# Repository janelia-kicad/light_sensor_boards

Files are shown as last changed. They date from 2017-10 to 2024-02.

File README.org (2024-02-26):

#+TITLE: light_sensor_boards
#+AUTHOR: Peter Polidoro
#+EMAIL: peter@polidoro.io

* Repository Information
- Name: light_sensor_boards
- Synopsis: Measures fly wingbeats (wing tachometer) using IR light reflected from flapping fly wings.
- URL: https://github.com/janelia-kicad/light_sensor_boards
- Author: Peter Polidoro
- Email:
  - polidorop@janelia.hhmi.org
  - peter@polidoro.io
- License: Janelia Open-Source Hardware
- Version: 2.0
- Release Date: July 2015
- Paper References:
  - Kim, A., Fitzgerald, J. & Maimon, G. Cellular evidence for efference copy in
    Drosophila visuomotor processing. Nat Neurosci 18, 1247–1255 (2015).
    https://doi.org/10.1038/nn.4083
  - David P. Goodman, Abby Eldredge, Catherine R. von Reyn, A novel assay to
    evaluate action selection in escape behavior, Journal of Neuroscience
    Methods, Volume 304, 2018, Pages 154-161, ISSN 0165-0270,
    https://doi.org/10.1016/j.jneumeth.2018.04.019
  - Suver et al., Active antennal movements in Drosophila can tune wind
    encoding, Current Biology (2023), https://doi.org/10.1016/j.cub.2023.01.020

** Description

These light sensor boards, or "wing tachometer”, combine to form a small
electro-optical device that uses reflected infrared light from the fly’s
wingbeats to generate an oscillating voltage signal. The oscillation frequency
of the voltage signal matches, and thus allows one to measure, the tethered
fly's wingbeat frequency.

This device is useful for plate (rather than pin) tethered flight experiments,
because with plate-glued flies, one cannot extract the wingbeat frequency via a
classical wingbeat analyzer. Microphones have also been used for extracting
wingbeat frequency, but they require a quiet room. This wingbeat detector is
immune to audible noise and only requires an infrared light source, often
already present on flight rigs for video recording.

One end of a small diameter light guide is mounted near the fly and aimed at the
wings. The other end of the light guide is in a small enclosure containing an
optical filter and printed circuit board and can be mounted off to the side of
the rig wherever there is room.

The light guide brings light reflected off of the wings down to a photodiode on
a circuit board, after passing through an optical filter to remove the unwanted
wavelengths of light. Amplifiers and filters on the circuit board convert the
tiny amounts of current from the photodiode into an oscillating voltage signal,
with a frequency range of several hundred Hertz and a magnitude range of several
Volts.

The oscillating voltage signal can be fed into a data acquisition card,
oscilloscope, and/or a speaker for recording and instant feedback on fly
wingbeat frequency. Using a threshold, the signal can be used as a simple
boolean that indicates whether the tethered animal is flying or not for
triggering experiments or synchronizing the data collection.

This device was first created at Caltech in the Dickinson lab in collaboration
with Gaby Maimon around 2010. It has transformed over several generations,
getting smaller and more robust each iteration. It has been used on rigs in
multiple universities and research institutes and has been referenced in several
papers. Version 2 was designed in collaboration with Sung Soo Kim and the Card
lab at Janelia Research Campus.

These boards have been deprecated and some parts are now difficult to purchase
or are obsolete.

The files in this repository are archived for reference.

* opt101 + power_signal

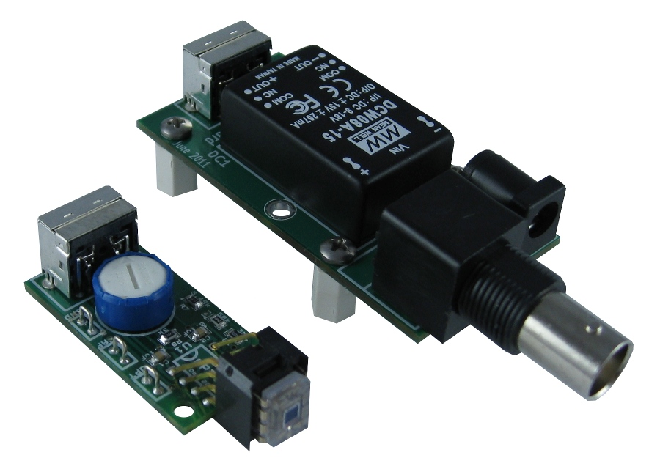
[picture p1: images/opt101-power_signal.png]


* opt101 + power_signal_compare

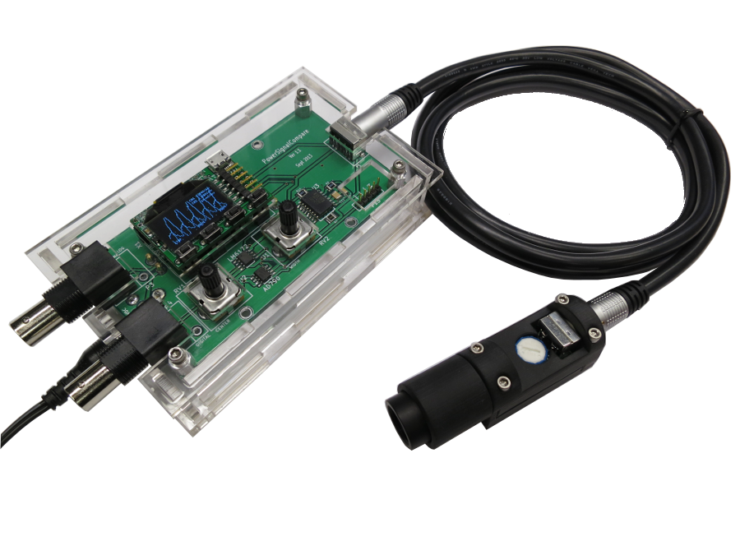
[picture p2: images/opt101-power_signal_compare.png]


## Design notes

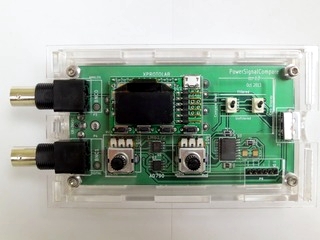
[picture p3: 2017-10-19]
light_sensor_boards/images/light_sensor_boards_19_s.jpg

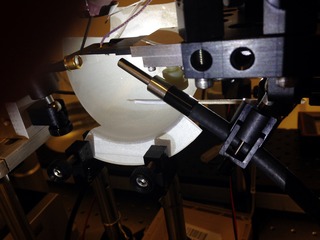
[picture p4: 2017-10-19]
light_sensor_boards/images/light_sensor_boards_24_s.jpg

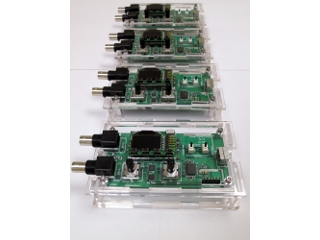
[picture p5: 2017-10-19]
light_sensor_boards/images/light_sensor_boards_20_s.jpg

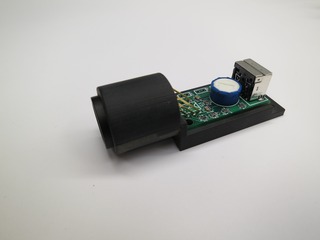
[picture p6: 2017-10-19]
light_sensor_boards/images/light_sensor_boards_06_s.jpg

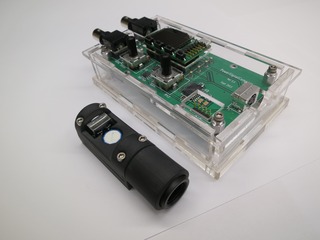
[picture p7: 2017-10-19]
light_sensor_boards/images/light_sensor_boards_02_s.jpg

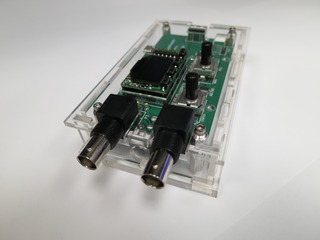
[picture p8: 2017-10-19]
light_sensor_boards/images/light_sensor_boards_12_s.jpg

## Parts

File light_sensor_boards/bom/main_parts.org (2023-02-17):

| Descripition                                                | Digi-Key Part Number |
|-------------------------------------------------------------+----------------------|
| CONN RCPT FMALE MINI DIN 4P SLDR                            | CP-2245-ND           |
| CBL 4POS MALE TO MALE 4.92'                                 | AE10074-ND           |
| CONN PWR JACK 2X5.5MM SOLDER                                | CP-063AH-ND          |
| DC DC CONVERTER 5V +/-15V 11W                               | 811-1827-5-ND        |
| IC FILTER 100KHZ UNIV 16SOIC                                | UAF42AU-ND           |
| TRIMMER 10K OHM 1W PC PIN TOP                               | 3345P-103-ND         |
| Optical Sensor Ambient 650nm Voltage 8-DIP (0.300", 7.62mm) | 296-23090-5-ND       |
| CONN IC DIP SOCKET 8POS GOLD                                | A117-ND              |

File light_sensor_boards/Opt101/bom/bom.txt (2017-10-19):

-*- mode:org -*-

# Opt101.lst
| ref | value  |
|-----+--------|
| C1  | 0.1uF  |
| C2  | 0.1uF  |
| C3  | 0.1uF  |
| C4  | 0.1uF  |
| J1  | DIN_4  |
| PP1 | OPT    |
| PP2 | UAF    |
| PP3 | GND    |
| R1  | 3M     |
| R2  | 42.2k  |
| R3  | 2.55M  |
| R4  | 2.55M  |
| R5  | 10     |
| R6  | 50k    |
| R7  | 5.49k  |
| R8  | 5k     |
| RV1 | 10k    |
| U1  | OPT101 |
| U3  | UAF42  |

# Bill of Materials
| ! | part  | description                     | vendor       | part number      | quantity |  cost |
|---+-------+---------------------------------+--------------+------------------+----------+-------|
|   | PCB   | OPT101 2.0                      | protoexpress | afv1-32881       |        1 | 35.00 |
|   | C1-4  | CAP CERM .1UF 10% 50V X7R 0805  | digikey      | 478-1395-1-ND    |        4 |  0.05 |
|   | J1    | CONN MINI-DIN 4PIN R/A SLIM PCB | digikey      | CP-2245-ND       |        1 |  1.82 |
|   | PP1-3 | JUMPER WIRE 0.1" LONG           | digikey      | 923345-01-ND     |        3 |  0.07 |
|   | R1    | RES 3.00M OHM 1/8W 1% 0805 SMD  | digikey      | 541-3.00MCCT-ND  |        1 |  0.09 |
|   | R2    | RES 42.2K OHM 1/8W 1% 0805 SMD  | digikey      | P42.2KCCT-ND     |        1 |  0.07 |
|   | R3,4  | RES 2.55M OHM 1/8W 1% 0805 SMD  | digikey      | 311-2.55MCRCT-ND |        2 |  0.03 |
|   | R5    | RES 10.0 OHM 1/8W 1% 0805 SMD   | digikey      | P10.0CCT-ND      |        1 |  0.07 |
|   | R6    | RES 49.9K OHM 1/8W 1% 0805 SMD  | digikey      | P49.9KCCT-ND     |        1 |  0.07 |
|   | R7    | RES 5.49K OHM 1/8W 1% 0805 SMD  | digikey      | P5.49KCCT-ND     |        1 |  0.07 |
|   | R8    | RES 4.99K OHM 1/8W 1% 0805 SMD  | digikey      | P4.99KCCT-ND     |        1 |  0.07 |
|   | RV1   | TRIMMER 10K OHM 1W TH           | digikey      | 3345P-103-ND     |        1 | 13.02 |
|   | U1    | IC PHOTODIODE/AMPLIFIER 8 DIP   | digikey      | 296-23090-5-ND   |        1 |  6.88 |
|   | U1    | IC SOCK 8 PIN VERT GOLD .300    | digikey      | A117-ND          |        1 |  6.29 |
|   | U3    | IC UNIV ACTIVE FILTER 16-SOIC   | digikey      | UAF42AU-ND       |        1 | 16.61 |
|---+-------+---------------------------------+--------------+------------------+----------+-------|
| # | total |                                 |              |                  |          | 80.53 |
#+TBLFM: @17$7=(@I$quantity..@II$quantity)*(@I$cost..@II$cost);%.2f;N

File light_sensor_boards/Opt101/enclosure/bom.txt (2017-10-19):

-*- mode:org -*-

# Bill of Materials
| ! | description                                                                            | vendor       | part number | quantity |   cost |
|---+----------------------------------------------------------------------------------------+--------------+-------------+----------+--------|
|   | SM05 Lens Tube, 0.5" Thread Depth                                                      | thorlabs     | SM05L05     |        1 |  13.75 |
|   | Liquid Light Guide Ø3 mm Core, 4' (1.2 m) Length                                       | thorlabs     | LLG0338-4   |        1 | 345.00 |
|   | Ø3 mm LLG to SM1 Adapter                                                               | thorlabs     | AD3LLG      |        1 |  30.00 |
|   | Adapter with External SM05 Threads and Internal SM1 Threads                            | thorlabs     | SM1A1       |        1 |  19.75 |
|   | Universal probe holder                                                                 | siskiyou     | MXB         |        1 | 200.00 |
|   | 850nm High Performance Longpass Filter 12.5mm Dia                                      | edmundoptics | 66-228      |        1 | 150.00 |
|   | 18-8 Stainless Steel Socket Head Cap Screw, 4-40 Thread, 3/4" Length                   | mcmaster     | 92196A113   |        4 |   0.06 |
|   | 18-8 Stainless Steel Machine Screw Hex Nut, 4-40 Thread Size, 1/4" Width, 3/32" Height | mcmaster     | 91841A005   |        4 |   0.03 |
|---+----------------------------------------------------------------------------------------+--------------+-------------+----------+--------|
| # | total                                                                                  |              |             |          | 758.86 |
#+TBLFM: @10$6=(@I$quantity..@II$quantity)*(@I$cost..@II$cost);%.2f;N

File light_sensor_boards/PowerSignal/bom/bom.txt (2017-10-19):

-*- mode:org -*-

# PowerSignal.lst
| ref | value        |
|-----+--------------|
| C1  | 10uF         |
| C2  | 1uF          |
| C3  | 10uF         |
| C4  | 1uF          |
| C5  | 0.1uF        |
| C6  | 0.1uF        |
| C7  | 0.1uF        |
| DC1 | DCW08        |
| P1  | DIN_4_SHIELD |
| P2  | BNC          |
| P3  | 9-18VDC      |
| P4  | CONN_1       |
| P5  | CONN_1       |
| P6  | CONN_1       |
| P7  | CONN_1       |
| P8  | CONN_1       |
| P9  | CONN_1       |
| P10 | CONN_1       |
| R1  | 634          |
| U1  | BUF634       |

# Bill of Materials
| ! | part  | description                      | vendor       | part number    | quantity |  cost |
|---+-------+----------------------------------+--------------+----------------+----------+-------|
|   | PCB   | PowerSignal 2.1                  | protoexpress | afv1-60094     |        1 | 34.50 |
|   | C1,3  | CAP CER 10UF 50V X7S 1210        | digikey      | 445-4536-1-ND  |        2 |  1.24 |
|   | C2,4  | CAP CER 1.0UF 50V 10% X7R 1210   | digikey      | 490-1863-1-ND  |        2 |  0.48 |
|   | C5-7  | CAP CERM .10UF 10% 50V X7R 1210  | digikey      | 478-3586-1-ND  |        3 |  0.73 |
|   | DC1   | DC-DC 2 Output 15 Volt-15 Volt   | jameco       | 1953364        |        1 | 19.95 |
|   | P1    | CONN MINI-DIN 4PIN R/A SLIM PCB  | digikey      | CP-2245-ND     |        1 |  1.82 |
|   | P1    | S-VIDEO 6'CABLE,2X MALE PLUGS    | jameco       | 228591         |        1 |  2.15 |
|   | P2    | CONN SOCKET BNC R/A 50 OHM PCB   | digikey      | A97555-ND      |        1 |  2.30 |
|   | P3    | Male 2 Position 6mm 2 Terminal   | jameco       | 137673         |        1 |  0.45 |
|   | P3    | AC/DC Power Supply 12V 1A 12W    | jameco       | 252824         |        1 | 12.95 |
|   | P4-10 | STDOFF HEX FLA-RET 4-40 .375"L   | digikey      | 8440BK-ND      |        5 |  0.84 |
|   | P4-10 | SCREW MACHINE PHIL 4-40X1/4 SS   | digikey      | H703-ND        |        5 |  0.05 |
|   | R1    | RES 634 OHM 1/4W 1% 1210 SMD     | digikey      | RHM634BDCT-ND  |        1 |  0.36 |
|   | U1    | IC OPAMP BUFFER 180MHZ SGL 8SOIC | digikey      | 296-24142-1-ND |        1 |  9.28 |
|---+-------+----------------------------------+--------------+----------------+----------+-------|
| # | total |                                  |              |                |          | 93.84 |
#+TBLFM: @16$7=(@I$quantity..@II$quantity)*(@I$cost..@II$cost);%.2f;N

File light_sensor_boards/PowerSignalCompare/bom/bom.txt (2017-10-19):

-*- mode:org -*-

# PowerSignalCompare.lst
| ref | value             |
|-----+-------------------|
| C1  | 22uF              |
| C2  | 22uF              |
| C3  | 22uF              |
| C4  | 47uF              |
| C5  | 0.1uF             |
| C6  | 0.1uF             |
| C7  | 0.1uF             |
| C8  | 0.1uF             |
| C9  | 0.1uF             |
| C10 | 0.1uF             |
| C11 | 0.1uF             |
| C12 | 0.1uF             |
| C13 | 0.1uF             |
| C14 | 0.1uF             |
| D1  | 9.1V_ZENER        |
| D2  | 9.1V_ZENER        |
| P1  | DIN_4_SHIELD      |
| P2  | 18-36VDC          |
| P3  | BNC0              |
| P4  | BNC1              |
| P5  | CONN_1            |
| P6  | CONN_1            |
| P7  | CONN_1            |
| P8  | CONN_1            |
| P9  | CONN_6            |
| R1  | 1k                |
| R2  | 1k                |
| R3  | 220               |
| R4  | 220               |
| R5  | 634               |
| R6  | 510               |
| R7  | 50k               |
| R8  | 44.2k             |
| R9  | 402k              |
| R10 | 402k              |
| RV1 | 10k               |
| RV2 | 10k               |
| S1  | TWR_TRIPLE_SUPPLY |
| SW1 | DISPLAY           |
| SW2 | COMPARE_INPUT     |
| U1  | LM6172            |
| U2  | AD790             |
| U3  | UAF42             |
| U4  | ISL55004          |
| X1  | XPROTOLAB         |

# Bill of Materials
| ! | part  | description                      | vendor      | part number         | quantity |   cost |
|---+-------+----------------------------------+-------------+---------------------+----------+--------|
|   | PCB   | PowerSignalCompare_v1.3          | pcbuniverse |                     |        1 |      0 |
|   | C1    | CAP TANT 22UF 50V 20% 2917       | digikey     | 399-9752-1-ND       |        1 |   5.45 |
|   | C2-3  | CAP TANT 22UF 20V 10% 1210       | digikey     | 478-3095-1-ND       |        2 |   1.27 |
|   | C4    | CAP TANT 47UF 10V 20% 1210       | digikey     | 478-3132-1-ND       |        1 |   1.24 |
|   | C5-14 | CAP CERM .10UF 10% 50V X7R 1210  | digikey     | 478-3586-1-ND       |       10 |   0.34 |
|   | D1-2  | DIODE ZENER 9.1V 250MW TO236AB   | digikey     | 568-7102-1-ND       |        2 |   0.49 |
|   | P1    | CONN MINI-DIN 4PIN R/A SLIM PCB  | digikey     | CP-2245-ND          |        1 |   1.79 |
|   | P1    | CABLE VIDEO S-VHS HI QUAL 1.5M   | digikey     | AE10074-ND          |        1 |   8.34 |
|   | P2    | CONN PWR JACK DC 2.1X5.5 8A T/H  | digikey     | CP-063AH-ND         |        1 |   1.78 |
|   | P2    | TRANSFORMER DESK TOP 24V 40W     | digikey     | T1206-P5P-ND        |        1 |  21.76 |
|   | P3-4  | CONN SOCKET BNC R/A 50 OHM PCB   | digikey     | A97555-ND           |        2 |   2.62 |
|   | P9    | CONN HEADER 6POS .100" SGL GOLD  | digikey     | SAM1031-06-ND       |        1 |   0.95 |
|   | R1-2  | RES 1K OHM 1/4W 1% 1210 SMD      | digikey     | RHM1.00KBDCT-ND     |        2 |   0.23 |
|   | R3-4  | RES 220 OHM 1/4W .1% 1210 SMD    | digikey     | P220QCT-ND          |        2 |   1.10 |
|   | R5    | RES 634 OHM 1/4W 1% 1210 SMD     | digikey     | RHM634BDCT-ND       |        1 |   0.23 |
|   | R6    | RES 510 OHM 1/4W .1% 1210 SMD    | digikey     | P510QCT-ND          |        1 |   1.10 |
|   | R7    | RES 49.9K OHM 1/4W 1% 1210 SMD   | digikey     | RHM49.9KBDCT-ND     |        1 |   0.23 |
|   | R8    | RES 44.2K OHM 1/2W 1% 1210 SMD   | digikey     | P44.2KAACT-ND       |        1 |   0.51 |
|   | R9-10 | RES 402K OHM 1/2W 1% 1210 SMD    | digikey     | P402KAACT-ND        |        2 |   0.51 |
|   | RV1-2 | POT 10K OHM 1/8W CARB VERTICAL   | digikey     | CT2265-ND           |        2 |   1.55 |
|   | S1    | CONV DC/DC TRI OUT 5,15,-15V     | digikey     | 811-1827-5-ND       |        1 |  75.60 |
|   | S1    | CONN RECEPT PIN .032-.046" .296" | digikey     | ED90531-ND          |        5 |   1.04 |
|   | SW1-2 | SWITCH TOGGLE SPDT 0.4VA 20V     | digikey     | CKN1784CT-ND        |        2 |   5.63 |
|   | U1    | IC AMP DUAL HI SPD LP V FB 8SOIC | digikey     | LM6172IMX/NOPBCT-ND |        1 |   3.94 |
|   | U2    | IC COMPARATOR PREC W/LATCH 8SOIC | digikey     | AD790JRZ-REEL7CT-ND |        1 |   8.61 |
|   | U3    | IC UNIV ACTIVE FILTER 16-SOIC    | digikey     | UAF42AU-ND          |        1 |  14.95 |
|   | U4    | IC OPAMP QUAD 200MHZ 14-SOIC     | digikey     | ISL55004IBZ-ND      |        1 |   9.45 |
|   | X1    | CONN HEADER FMALE 12POS .1" GOLD | digikey     | S7045-ND            |        1 |   0.99 |
|   | X1    | CONN HEADER FEMALE 2POS .1" GOLD | digikey     | S7035-ND            |        4 |   0.49 |
|   | X1    | XMEGA Xprotolab                  | gabotronics | XMEGA Xprotolab     |        1 |  49.00 |
|---+-------+----------------------------------+-------------+---------------------+----------+--------|
| # | total |                                  |             |                     |          | 243.28 |
#+TBLFM: @32$7=(@I$quantity..@II$quantity)*(@I$cost..@II$cost);%.2f;N

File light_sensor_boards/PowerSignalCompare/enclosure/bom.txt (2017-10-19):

-*- mode:org -*-
# Bill of Materials
| ! | description                                                                                                  | vendor   | part number | quantity |  cost |
|---+--------------------------------------------------------------------------------------------------------------+----------+-------------+----------+-------|
|   | Optically Clear Cast Acrylic Sheet, 1/8" Thick, 12" x 12"                                                    | mcmaster | 8560K239    |        1 |  8.63 |
|   | Optically Clear Cast Acrylic Sheet, 1/4" Thick, 12" x 12"                                                    | mcmaster | 8560K354    |        1 | 16.36 |
|   | 18-8 Stainless Steel Socket Head Cap Screw, 4-40 Thread, 5/16" Length                                        | mcmaster | 92196A107   |        4 |  0.04 |
|   | 300 Series Stainless Steel NAS 620 Flat Washer, Number 4 Size, .21" OD, .01"-.02" Thickness, Dash Number C4L | mcmaster | 90945A710   |        4 |  0.01 |
|   | 18-8 Stainless Steel Male-Female Threaded Hex Standoff, 3/16" Hex, 1/2" Length, 4-40 Screw Size              | mcmaster | 91075A665   |        4 |  2.20 |
|   | 18-8 Stainless Steel Male-Female Threaded Hex Standoff, 3/16" Hex, 1/4" Length, 4-40 Screw Size              | mcmaster | 91075A655   |        4 |  2.15 |
|---+--------------------------------------------------------------------------------------------------------------+----------+-------------+----------+-------|
| # |                                                                                                              |          |             |          | 42.59 |
#+TBLFM: @8$6=(@I$quantity..@II$quantity)*(@I$cost..@II$cost);%.2f;N

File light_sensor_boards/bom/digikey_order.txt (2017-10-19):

12, 399-9752-1-ND
25, 478-3095-1-ND
12, 478-3132-1-ND
120, 478-3586-1-ND
25, CP-2245-ND
12, AE10074-ND
12, CP-063AH-ND
12, T1073-P5P-ND
25, A97555-ND
12, SAM1031-05-ND
25, RHM1.00KBDCT-ND
25, P220QCT-ND
25, RHM634BDCT-ND
25, P510QCT-ND
25, RHM49.9KBDCT-ND
25, P44.2KAACT-ND
25, P402KAACT-ND
25, CT2265-ND
12, 811-1827-5-ND
12, LM6172IMX/NOPBCT-ND
12, AD790JRZ-REEL7CT-ND
25, UAF42AU-ND
12, ISL55004IBZ-ND
20, S7045-ND
50, S7035-ND
100, 478-1395-1-ND
100, 541-3.00MCCT-ND  
100, P42.2KCCT-ND     
100, 311-2.55MCRCT-ND 
100, P10.0CCT-ND      
100, P49.9KCCT-ND     
100, P5.49KCCT-ND     
100, P4.99KCCT-ND     
20, 3345P-103-ND     
20, 296-23090-5-ND   
20, A117-ND

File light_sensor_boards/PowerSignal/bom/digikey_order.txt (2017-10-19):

20, 445-4536-1-ND
20, 490-1863-1-ND
20, 478-3586-1-ND
20, CP-2245-ND
20, A97555-ND
100, 8440BK-ND
100, H703-ND
20, RHM634BDCT-ND
20, 296-24142-1-ND

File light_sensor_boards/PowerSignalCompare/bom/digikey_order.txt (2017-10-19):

12, 399-9752-1-ND
25, 478-3095-1-ND
12, 478-3132-1-ND
200, 478-3586-1-ND
25, 568-7102-1-ND
12, CP-2245-ND
4, AE10074-ND
12, CP-063AH-ND
2, T1206-P5P-ND
25, A97555-ND
12, SAM1031-06-ND
25, RHM1.00KBDCT-ND
25, P220QCT-ND
25, RHM634BDCT-ND
25, P510QCT-ND
25, RHM49.9KBDCT-ND
25, P44.2KAACT-ND
25, P402KAACT-ND
30, CT2265-ND
10, 811-1827-5-ND
75, ED90531-ND
25, CKN1784CT-ND
15, LM6172IMX/NOPBCT-ND
15, AD790JRZ-REEL7CT-ND
12, UAF42AU-ND
12, ISL55004IBZ-ND
20, S7045-ND
75, S7035-ND

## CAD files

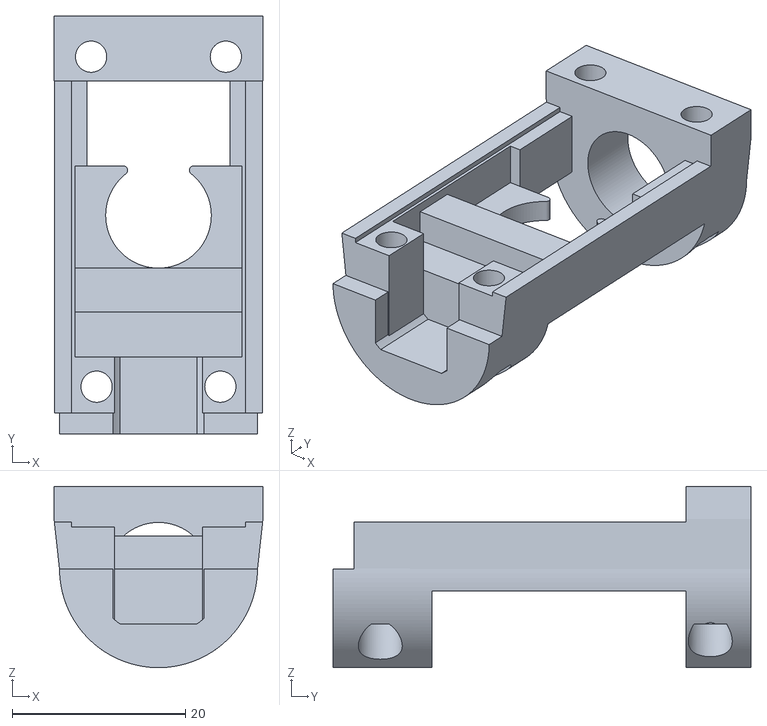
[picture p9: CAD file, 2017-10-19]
light_sensor_boards/Opt101/enclosure/Opt101EnclosureFront.stl
24.1 x 48.3 x 20.9

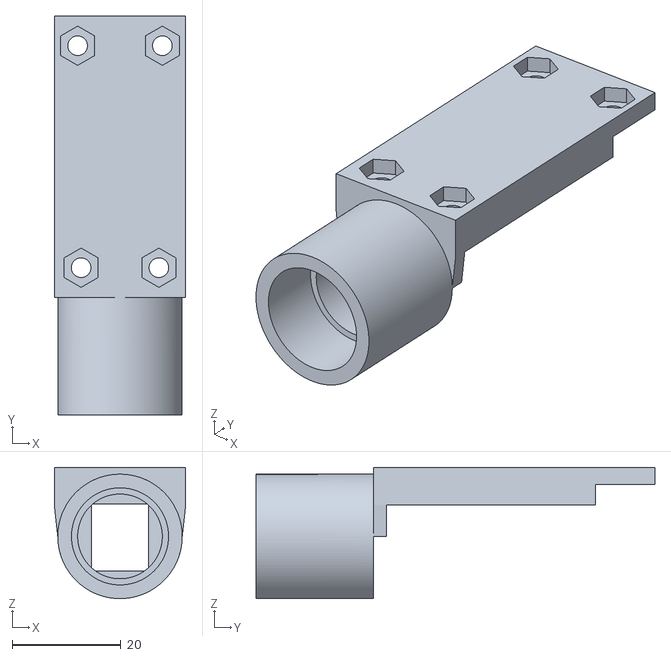
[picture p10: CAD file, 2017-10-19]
light_sensor_boards/Opt101/stl/Opt101EnclosureBack.stl
24.1 x 73.3 x 24.1

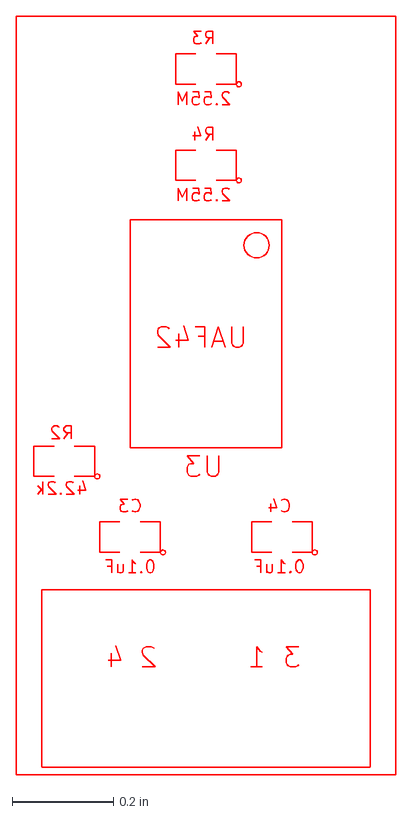
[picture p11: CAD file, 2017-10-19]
light_sensor_boards/Opt101/v2.0/dxf/Opt101-SilkS_Back.dxf
0.75 x 1.50 in

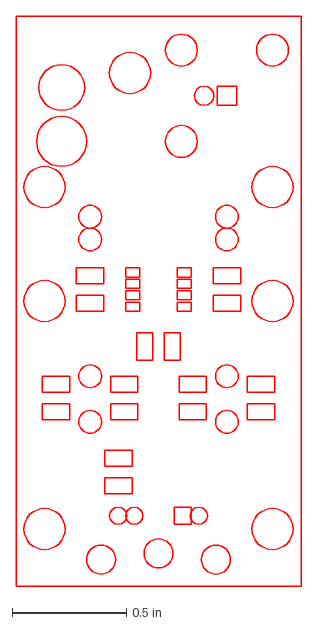
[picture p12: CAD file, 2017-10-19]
light_sensor_boards/PowerSignal/v2.1/dxf/PowerSignal-Mask_Back.dxf
1.25 x 2.50 in

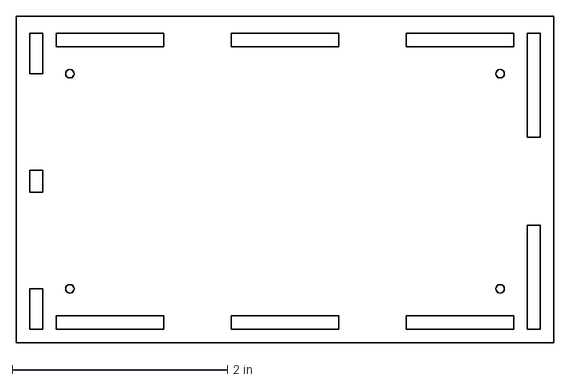
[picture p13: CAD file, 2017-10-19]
light_sensor_boards/PowerSignalCompare/enclosure/PowerSignalCompareEnclosure.25in.dxf
5.00 x 3.03 in

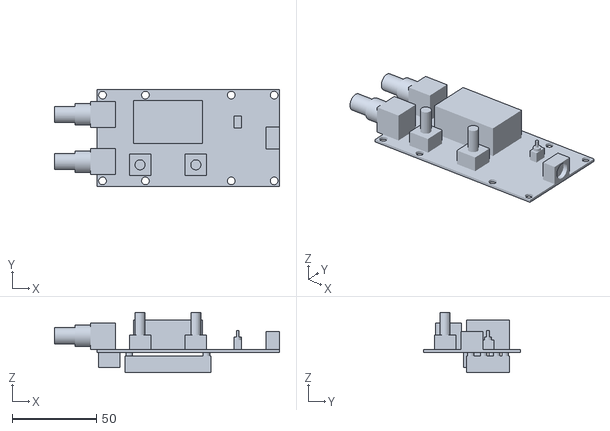
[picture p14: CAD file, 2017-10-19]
light_sensor_boards/PowerSignalCompare/stl/PowerSignalCompare.stl
133.2 x 57.1 x 35.8

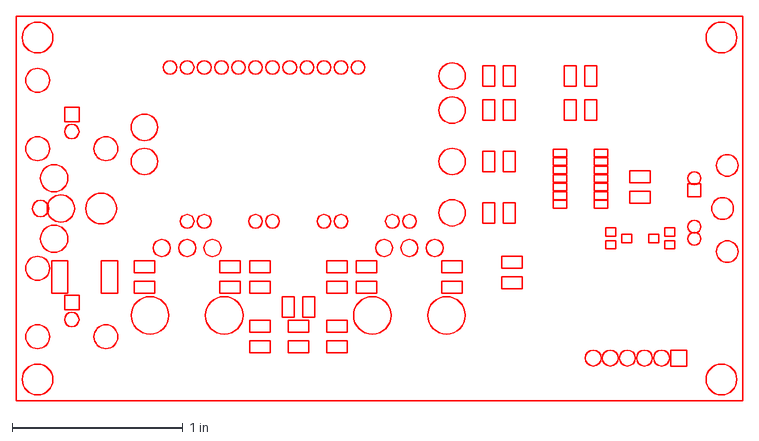
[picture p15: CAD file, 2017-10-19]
light_sensor_boards/PowerSignalCompare/v1.3/dxf/PowerSignalCompare-Mask_Back.dxf
4.25 x 2.25 in

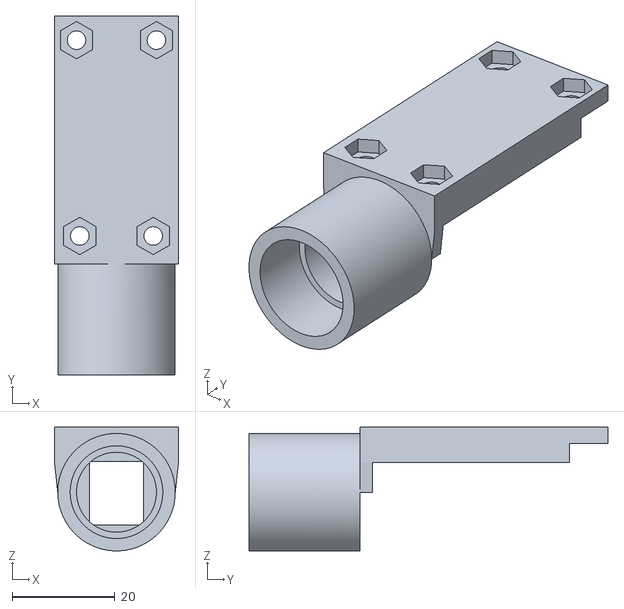
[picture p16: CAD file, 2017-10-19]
light_sensor_boards/Opt101/enclosure/Opt101EnclosureBack.stl
24.1 x 69.8 x 24.1

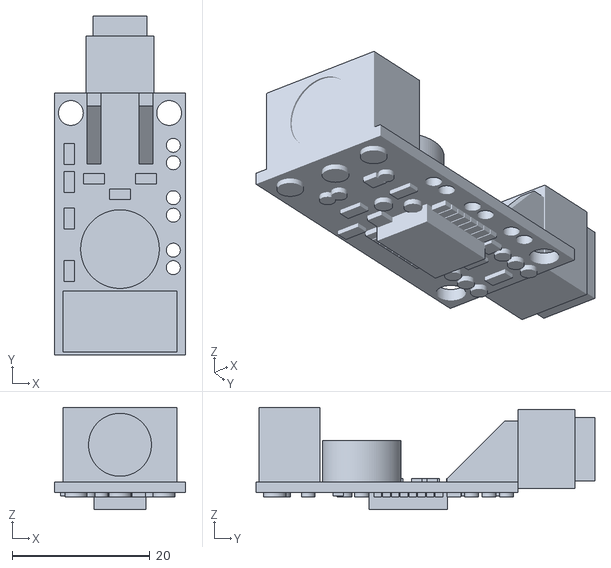
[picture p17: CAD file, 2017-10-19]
light_sensor_boards/Opt101/stl/Opt101.stl
19.1 x 49.3 x 14.9

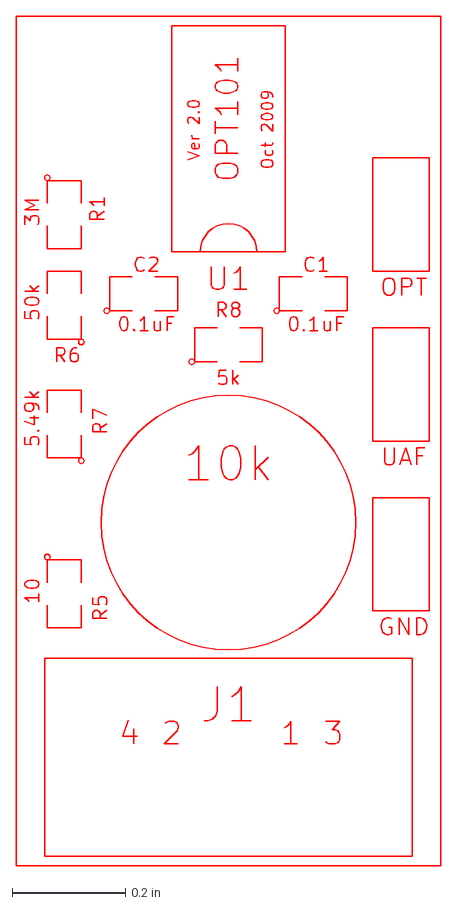
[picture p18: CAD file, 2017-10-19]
light_sensor_boards/Opt101/v2.0/dxf/Opt101-SilkS_Front.dxf
0.75 x 1.50 in

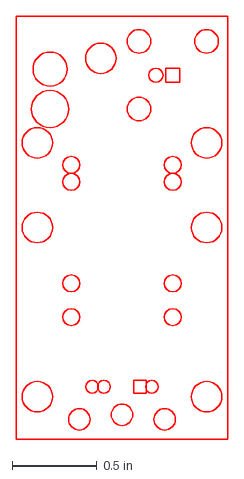
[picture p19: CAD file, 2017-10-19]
light_sensor_boards/PowerSignal/v2.1/dxf/PowerSignal-Mask_Front.dxf
1.25 x 2.50 in

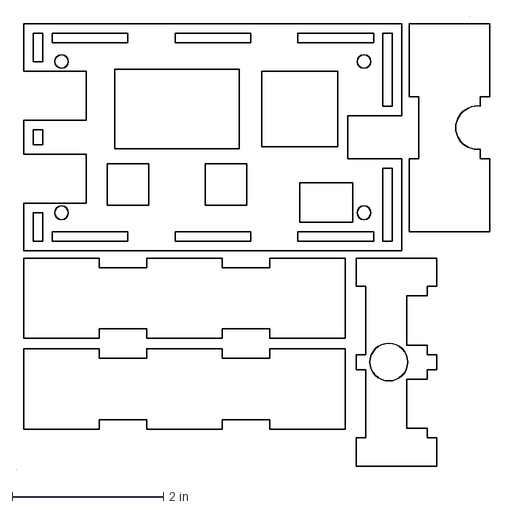
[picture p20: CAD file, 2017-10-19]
light_sensor_boards/PowerSignalCompare/enclosure/PowerSignalCompareEnclosure.125in.dxf
6.26 x 6.00 in

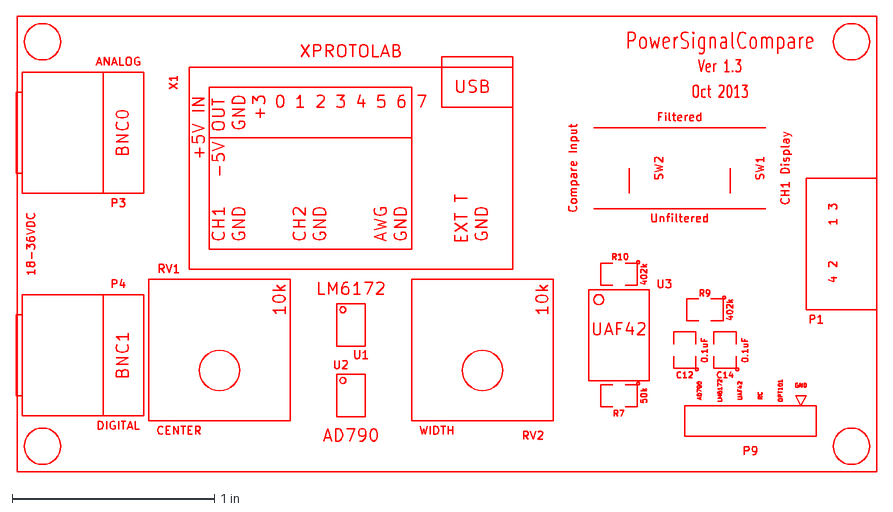
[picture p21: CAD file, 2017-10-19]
light_sensor_boards/PowerSignalCompare/v1.3/dxf/PowerSignalCompare-SilkS_Front.dxf
4.25 x 2.25 in

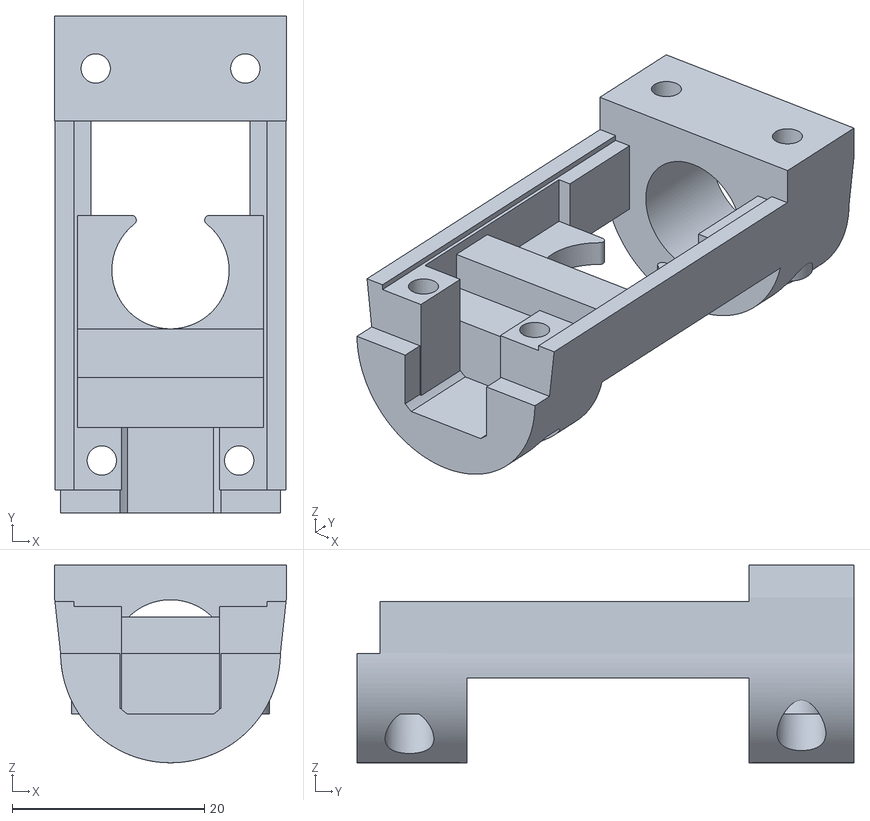
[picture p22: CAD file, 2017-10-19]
light_sensor_boards/Opt101/stl/Opt101EnclosureFront.stl
24.1 x 51.7 x 20.5

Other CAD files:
light_sensor_boards/Opt101/v2.0/dxf/Opt101-Mask_Front.dxf
light_sensor_boards/PowerSignal/v2.1/dxf/PowerSignal-SilkS_Front.dxf
light_sensor_boards/PowerSignalCompare/v1.3/dxf/PowerSignalCompare-Mask_Front.dxf
light_sensor_boards/Opt101/v2.0/dxf/Opt101-Mask_Back.dxf
light_sensor_boards/PowerSignal/v2.1/dxf/PowerSignal-SilkS_Back.dxf
light_sensor_boards/PowerSignalCompare/v1.0/dxf/PowerSignalCompare-Mask_Back.dxf
light_sensor_boards/PowerSignalCompare/v1.0/dxf/PowerSignalCompare-Mask_Front.dxf
light_sensor_boards/PowerSignalCompare/v1.0/dxf/PowerSignalCompare-SilkS_Back.dxf
light_sensor_boards/PowerSignalCompare/v1.0/dxf/PowerSignalCompare-SilkS_Front.dxf
light_sensor_boards/PowerSignalCompare/v1.1/dxf/PowerSignalCompare-Mask_Back.dxf
light_sensor_boards/PowerSignalCompare/v1.1/dxf/PowerSignalCompare-Mask_Front.dxf
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

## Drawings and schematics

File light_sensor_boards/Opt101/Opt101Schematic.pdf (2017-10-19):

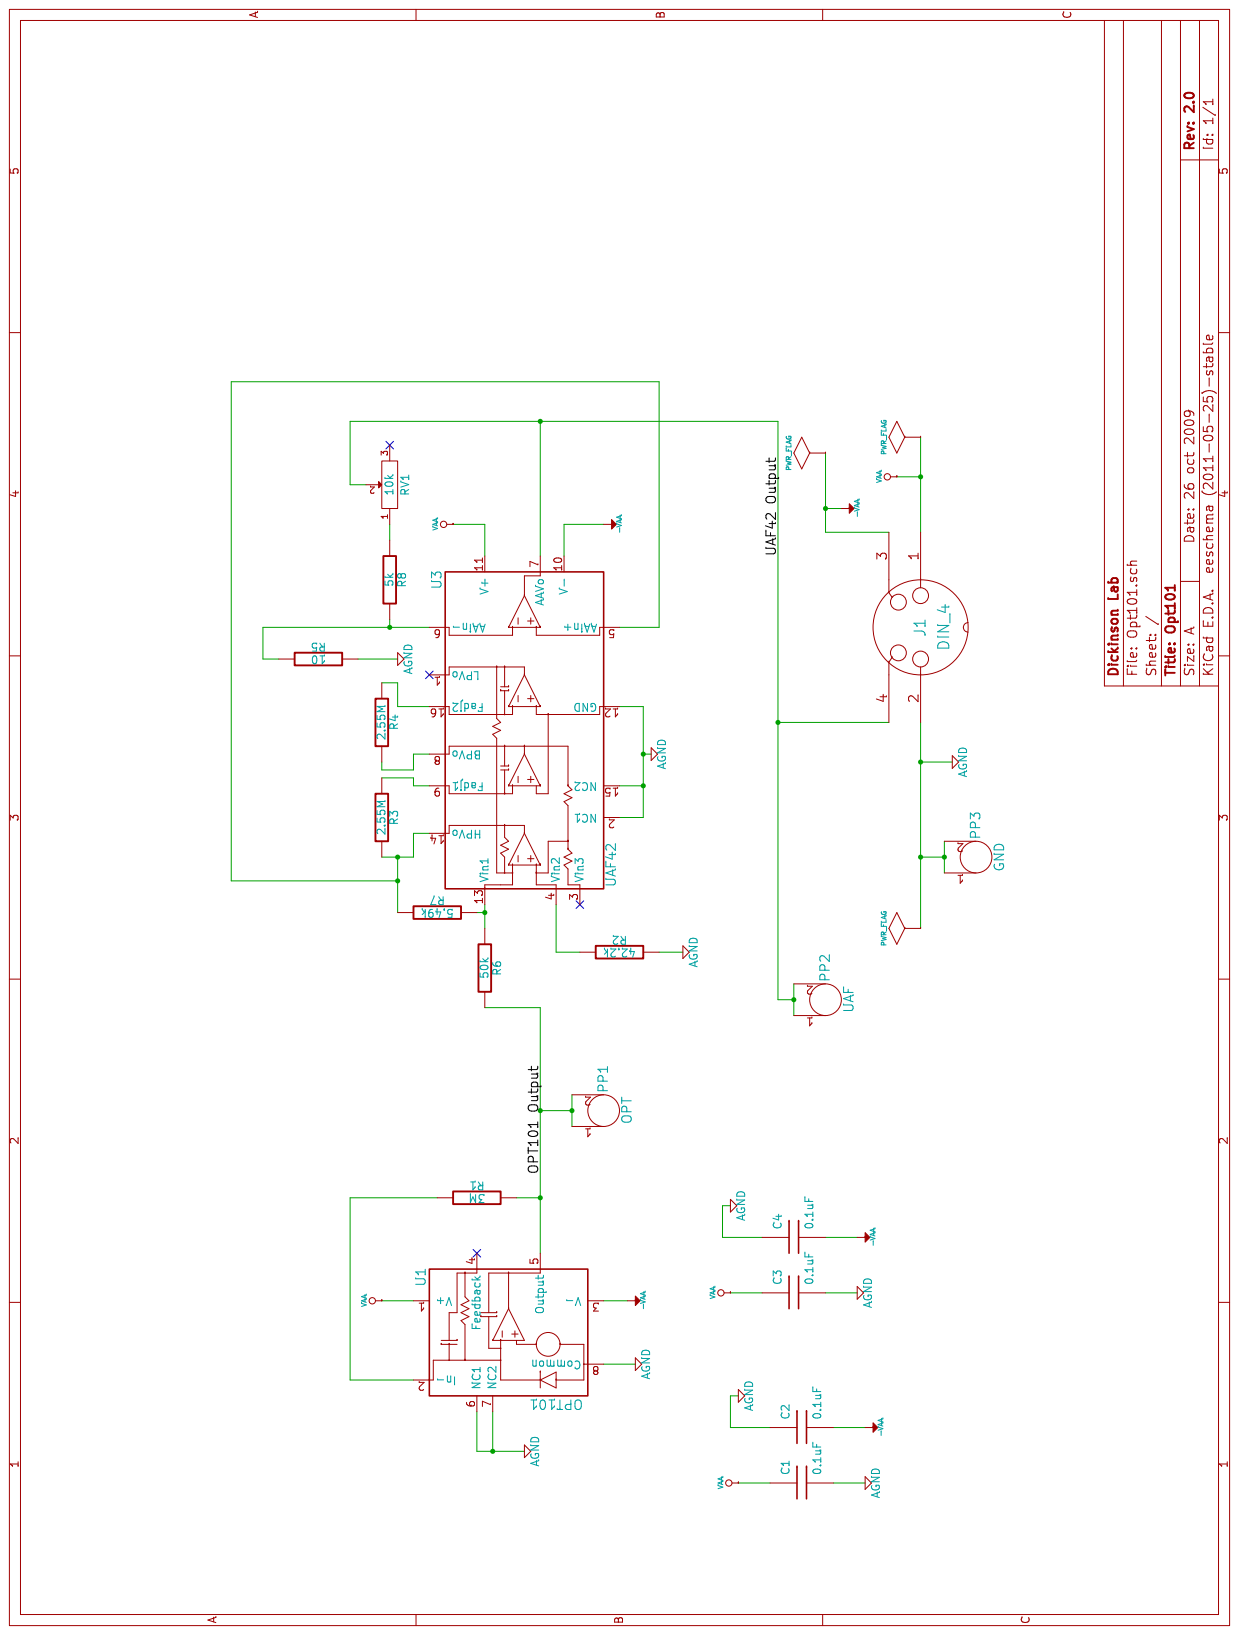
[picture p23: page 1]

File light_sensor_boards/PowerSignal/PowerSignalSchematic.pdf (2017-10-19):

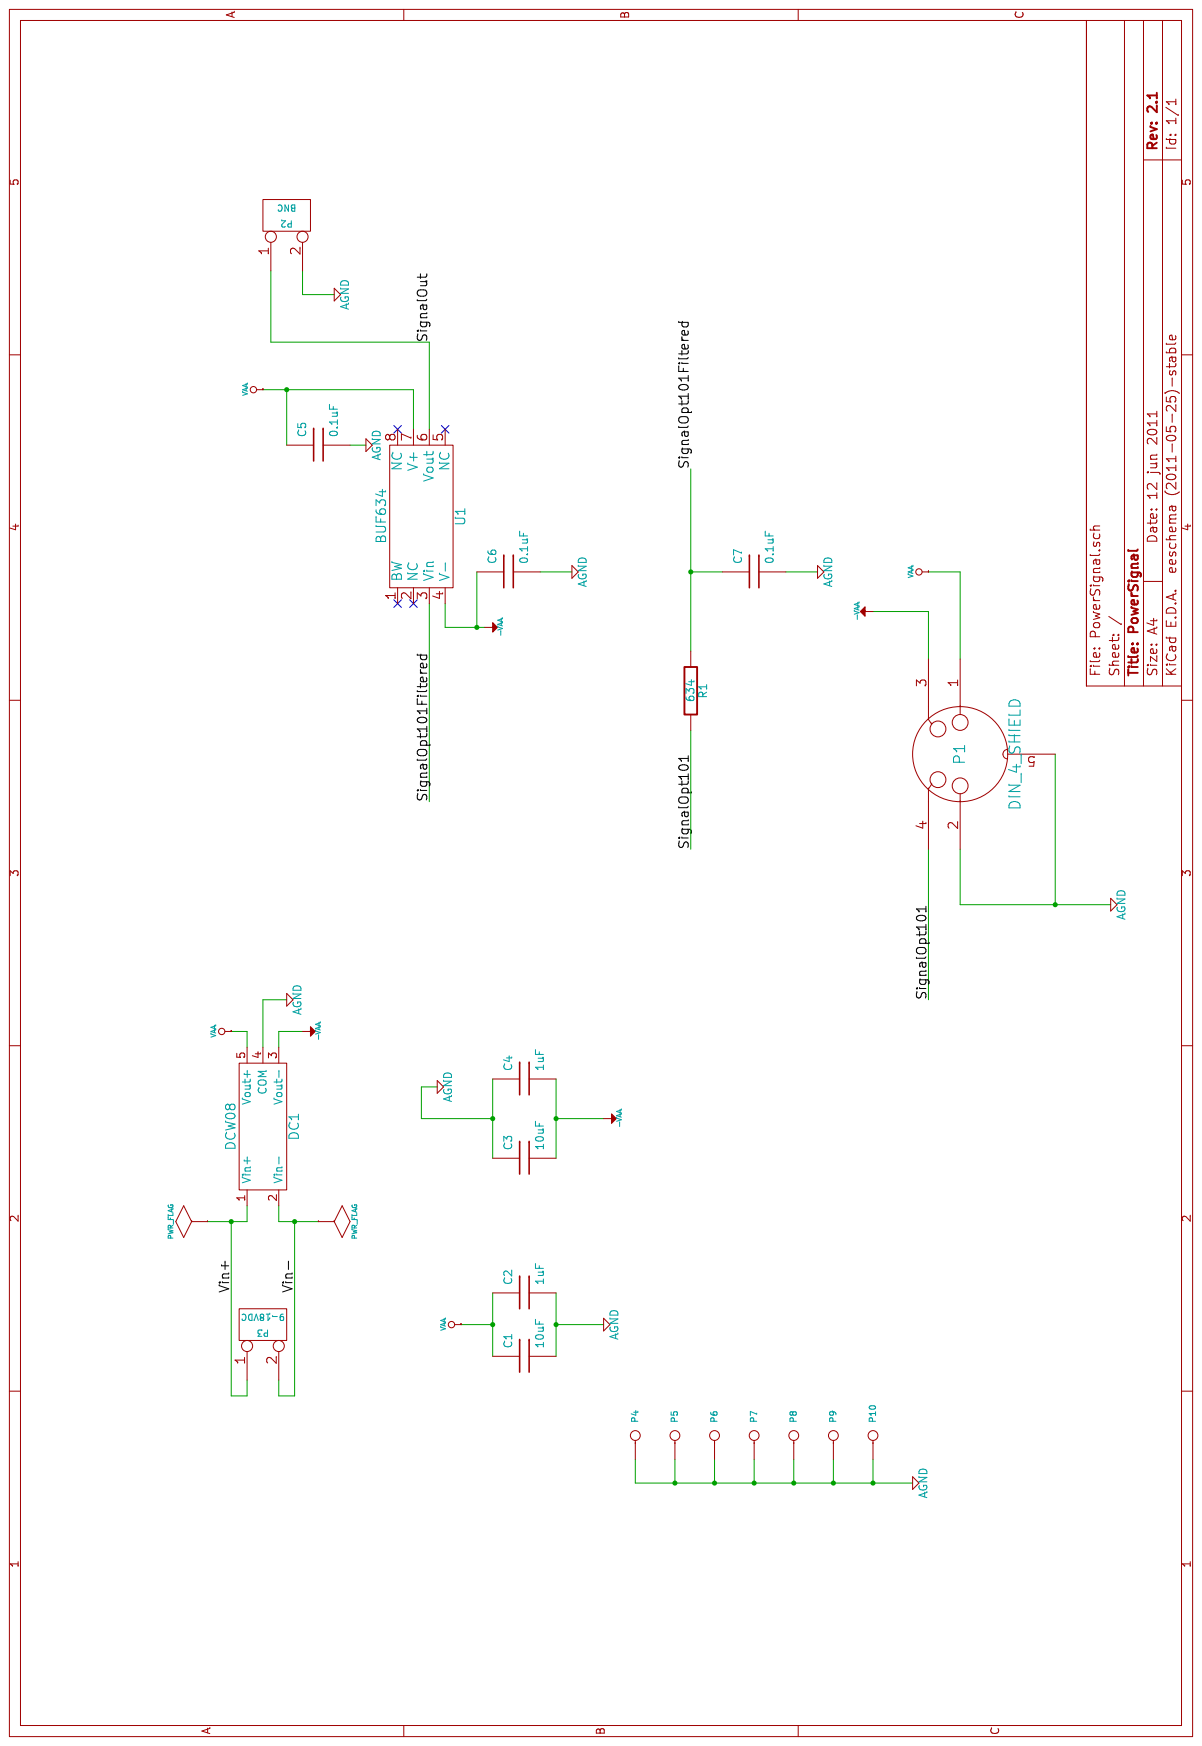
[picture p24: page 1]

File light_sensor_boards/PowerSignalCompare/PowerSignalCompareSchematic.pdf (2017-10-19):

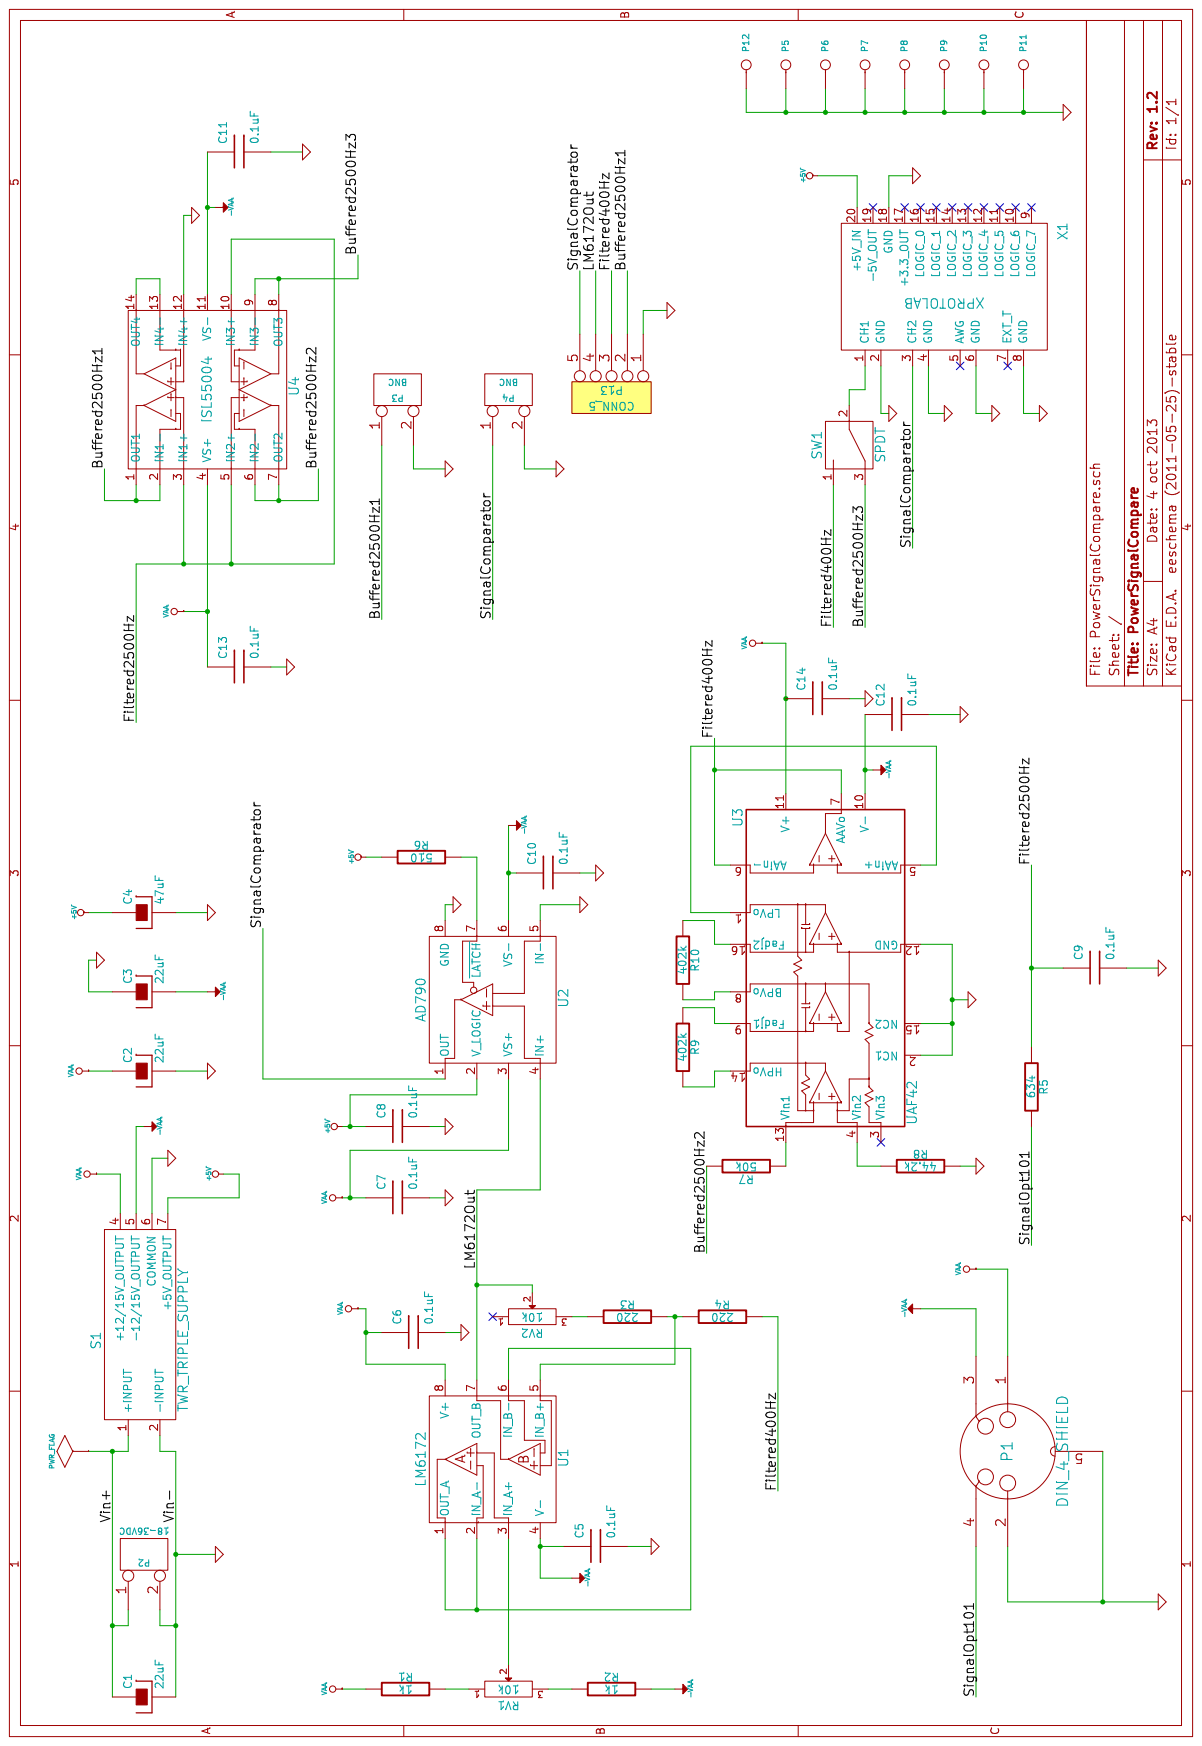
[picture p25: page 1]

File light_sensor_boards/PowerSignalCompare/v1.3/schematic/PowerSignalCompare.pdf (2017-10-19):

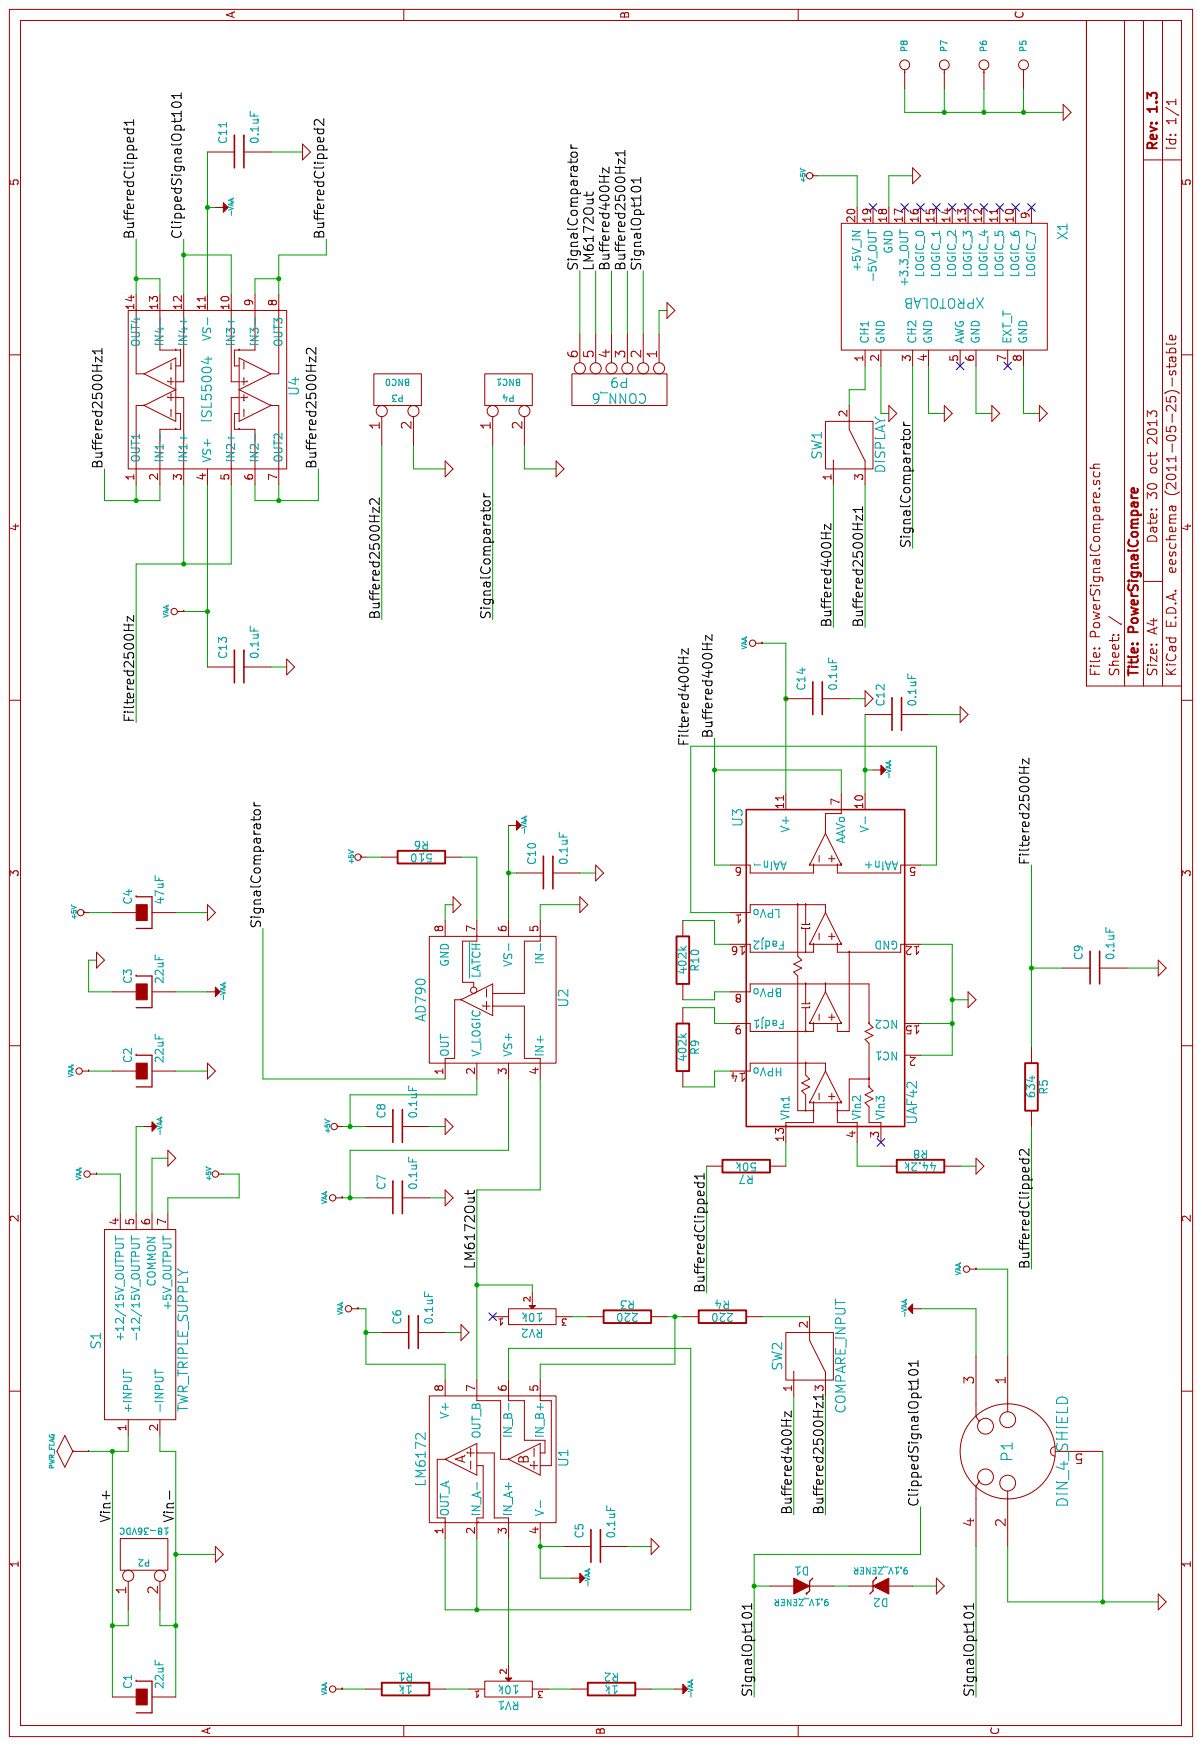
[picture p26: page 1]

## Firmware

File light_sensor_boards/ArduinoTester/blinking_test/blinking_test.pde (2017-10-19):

/*
  Analog Input
 Demonstrates analog input by reading an analog sensor on analog pin 0 and
 turning on and off a light emitting diode(LED)  connected to digital pin 13. 
 The amount of time the LED will be on and off depends on
 the value obtained by analogRead(). 
 
 The circuit:
 * Potentiometer attached to analog input 0
 * center pin of the potentiometer to the analog pin
 * one side pin (either one) to ground
 * the other side pin to +5V
 * LED anode (long leg) attached to digital output 13
 * LED cathode (short leg) attached to ground
 
 * Note: because most Arduinos have a built-in LED attached 
 to pin 13 on the board, the LED is optional.
 
 
 Created by David Cuartielles
 Modified 4 Sep 2010
 By Tom Igoe
 
 This example code is in the public domain.
 
 http://arduino.cc/en/Tutorial/AnalogInput
 
 */

int sensorPin = A0;    // select the input pin for the potentiometer
int ledPin = 9;      // select the pin for the LED
int sensorValue = 0;  // variable to store the value coming from the sensor
int sensorValueMin = 0;
int sensorValueMax = 1023;
int halfPeriodMin = 20;
int halfPeriodMax = 2;
int halfPeriod;

void setup() {
  // declare the ledPin as an OUTPUT:
  pinMode(ledPin, OUTPUT);  
}

void loop() {
  // read the value from the sensor:
  sensorValue = analogRead(sensorPin);
  halfPeriod = map(sensorValue,sensorValueMin,sensorValueMax,halfPeriodMin,halfPeriodMax);
  // turn the ledPin on
  digitalWrite(ledPin, HIGH);  
  // stop the program for <sensorValue> milliseconds:
  delay(halfPeriod);          
  // turn the ledPin off:        
  digitalWrite(ledPin, LOW);   
  // stop the program for for <sensorValue> milliseconds:
  delay(halfPeriod);                  
}

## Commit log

2017-10-19 Initial commit.
    [$savepcb.brd, Opt101-Mask_Back.dxf, Opt101-Mask_Front.dxf, Opt101-SilkS_Back.dxf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]
2017-10-19 Reorganized directories.
    [$savepcb.brd, Opt101-Mask_Back.dxf, Opt101-Mask_Front.dxf, Opt101-SilkS_Back.dxf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]
2017-10-20 Reorganized and removed outdated kicad files.
    [$savepcb.brd, Opt101.brd, Opt101.dsn, Opt101.sch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]
2022-07-11 Add kicad files
    [Opt101.brd, Opt101.sch, PowerSignal.brd, PowerSignal.sch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]
2023-02-17 Add project files
    [$savepcb.brd, Opt101-Mask_Back.dxf, Opt101-Mask_Front.dxf, Opt101-SilkS_Back.dxf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]
